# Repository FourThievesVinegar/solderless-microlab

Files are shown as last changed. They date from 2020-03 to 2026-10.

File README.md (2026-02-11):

# MicroLab

The MicroLab is an open-source, DIY, automated controlled lab reactor (CLR) that people can assemble with parts available online. We hope this will do for chemistry what the 3D printer did for manufacturing: provide a DIY, hackable, low-cost method to design and produce certain needful things that otherwise would be out of reach.

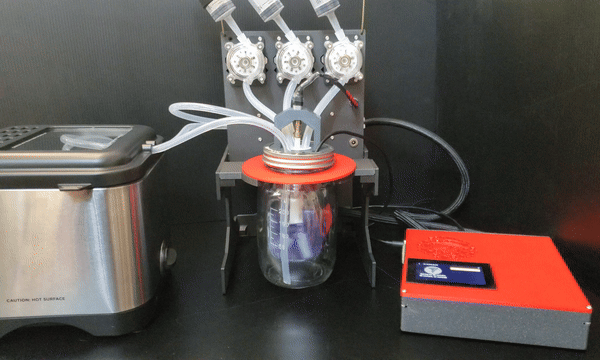
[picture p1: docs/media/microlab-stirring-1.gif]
MicroLab fully assembled with all units


## The MicroLab Suite

For the MicroLab to be accessible to the most people, it was developed as part of a hardware/software stack called the MicroLab Suite. The different software programs help take the information about a compound you want to make and translate it into a recipe (code) that the MicroLab runs to create the compound.

On the [About the MicroLab and MicroLab Suite](docs/motivation.md) page, you can find an introduction to the project with answers to common questions like:
- What the heck is a CLR?
- What's in the MicroLab Suite? 
- And...
- Why we are doing this at all?

MicroLab roadmap of major features for the next 2 versions. V 1.1: “Hello World” recipes complete, Open source reagent pumps, International BOMs, Printable / DIY alternatives for all scarce parts, Atmosphere control. v1.2: Raspberry Pi optional, Recipe repo launched, Auxiliary software suite comple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

In this repo:
```
solderless-microlab
├─ backend/ - Python files for the services that control the state and hardware
├─ design/  - Desktop wallpaper and other design files
├─ docker/  - Docker files 
├─ docs/    - Documentation for the project including build instructions, background, parts list, and troubleshooting
├─ gui/     - React app that runs the GUI 
├─ parts/   - 3d-printable part files for the 1.0+ version
├─ scripts/ - Scripts that start / stop services and flash the Arduino
│  ├─ disk-image - Scripts that build a MicroLab disk image
│  ├─ grbl       - Custom grbl code that allows the Arduino to control the hardware
```

## Architecture

### The Microlab stack

The Microlab is essentially a full-stack web application whose backend has access to control a set of hardware.

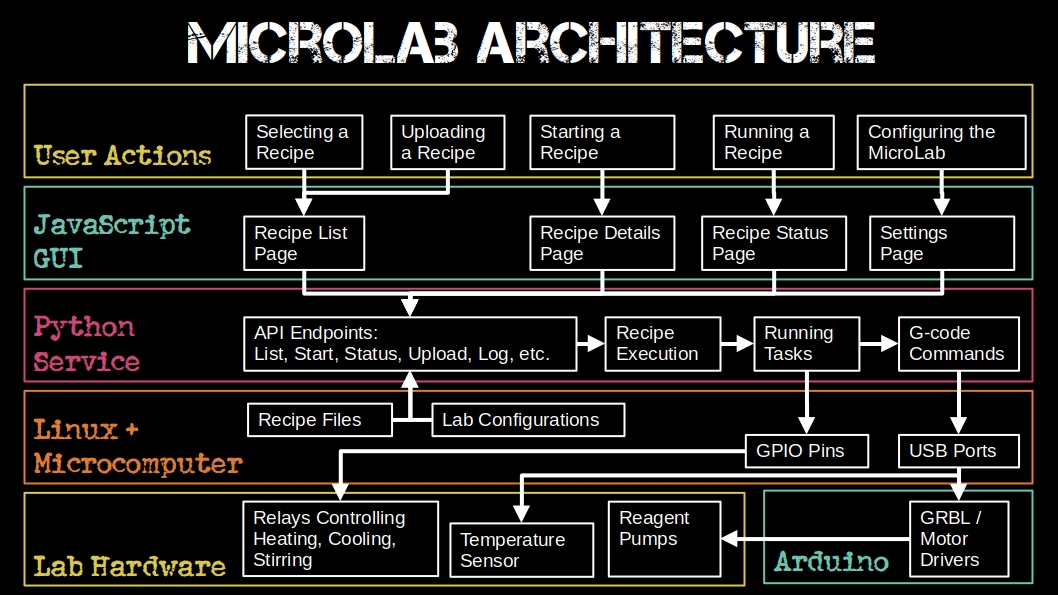
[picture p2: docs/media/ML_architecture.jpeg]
MicroLab architecture diagram. It shows how the user actions, javascript gui, python API, Linux OS, Raepberry Pi micro-computer, and Arduino microcontroller relate to one another.


### Running a Recipe

Running a recipe involves taking user input in the form of a recipe file and tapping on the touchscreen to perform a series of automated and manual tasks to execute a chemical reaction.

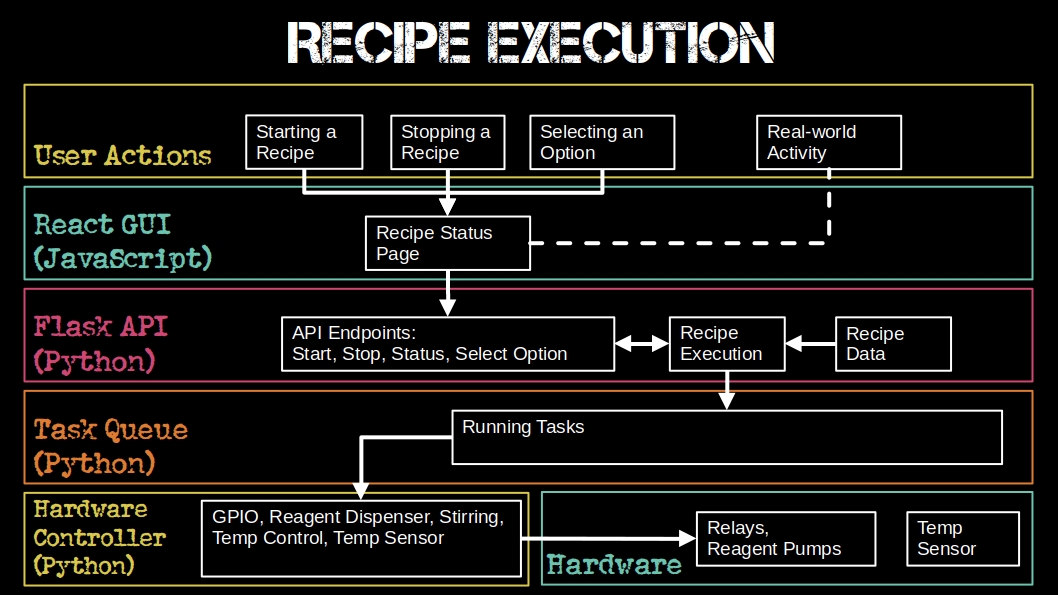
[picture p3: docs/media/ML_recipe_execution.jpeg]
MicroLab recipe flow diagram. It shows how the user actions, javascript gui, python API, python task queue, python hardware controller, and physical hardware relate to one another.


## Getting Started Making Your MicroLab

This section is for you if you want to build a MicroLab and start using it. We tried to make building the MicroLab friendly for folks newer to electronics, but you will need some knowledge and skills with electronics (or the patience to learn a few things).

- Learn [About the MicroLab and MicroLab Suite](docs/motivation.md) so you have an understanding of what you are building.
- **Start here for [How to build & use the MicroLab and MicroLab Suite](docs/index.md)**

## Getting Started Developing the MicroLab

This section is for you if you want to help develop the MicroLab and will need to tinker with the code base. If you're thinking about doing this, be sure to check out the [development wiki](https://github.com/FourThievesVinegar/solderless-microlab/wiki) and the [current issues](https://github.com/FourThievesVinegar/solderless-microlab/issues) planned for development.

You will need to get a copy of the MicroLab software, set up your development environment either with a Docker container, on a Pi, or locally on your computer.

### Installing the MicroLab software locally

Use the instructions below for a fresh install of the MicroLab software on your machine.

If you intend to construct a full MicroLab, [we recommend using our build scripts to make a disk image](https://github.com/FourThievesVinegar/microlab-image). You can also find the latest release of the disk image scripts in this repo in the `/scripts/disk-image` directory. We do not recommend running these scripts directly on the Raspberry Pi. See below if you want to run a development environment on another computer.

## Dev Environment Option 1: Docker Development

For ease of setup/experimentation we added docker containers for both the GUI and the API.
If you don't have docker-compose installed on your system you can install docker desktop following [these docs](https://docs.docker.com/compose/install/)

```bash
git clone https://github.com/FourThievesVinegar/solderless-microlab.git
cd solderless-microlab

## To run API & GUI
docker-compose up --build gui

## Alternatively
## To run just the API
docker-compose up --build api
```

If you're running docker with a hardware setup you'll need to edit docker-compose.yml and uncomment the lines specified in the file.

Docker-compose mounts `docker/microlab-docker.ini` local file as `/etc/microlab/microlab.ini` in the container. To modify microlab config
just edit `docker/microlab-docker.ini` file and restart the container in docker-compose.

For making local development simpler - `backend/` directory is also mounted as container's `/app` directory. Any local file change is automatically reflected in the container but in most cases you would also need to restart container anyway so the python processes load from updated files.

## Dev Environment Option 2: Laptop Setup

Clone the repo:

```bash
git clone https://github.com/FourThievesVinegar/solderless-microlab.git
cd solderless-microlab
```

### API Server

#### Install dependencies:

##### Python

(for Debian / Ubuntu)

```bash
sudo apt update
sudo apt install python3 python3-pip python-virtualenv python3-virtualenv
```

The backend is tested against CPython 3.9 to 3.13.

Note: some versions of Linux have dropped support for Python2 and `python-virtualenv`.

(for macOS)

```bash
brew update
brew install python3
pip3 install virtualenv
```

Set up a Python virtual environment:
virtualenv -p python3 --system-site-packages .venv

```bash
cd backend
virtualenv -p python3 --system-site-packages .venv
source .venv/bin/activate
(env) $ pip install -r requirements.txt
```

##### Install needed packages

(on the Pi)

```bash
sudo apt -y install screen git python3-flask python3-pip python3-serial

```

#### Start the server

```bash
(env) $ python main.py
```

### Web GUI

#### Install dependencies

(for Debian / Ubuntu)

Follow a guide to install yarn for Debian:

https://classic.yarnpkg.com/en/docs/install/#debian-stable

In summary:

```bash
curl -sS https://dl.yarnpkg.com/debian/pubkey.gpg | sudo apt-key add -
echo "deb https://dl.yarnpkg.com/debian/ stable main" | sudo tee /etc/apt/sources.list.d/yarn.list
sudo apt update
sudo apt install yarn
```

(for macOS)

```bash
brew update
brew install yarn
```

#### Run the GUI:

```bash
cd gui
yarn install
yarn start
```

The GUI will now be listening on port 3000.

## MicroLab Hardware Options

### Hardware Emulation

To run the software without a functioning hardware environment, go to the settings menu and change the "MicroLab Controller" setting to "simulation-pi" and "Lab Hardware Config" to "ftv_simulation_microlabv0.5.0"

### MicroLab Setup - Enabling SSH

If you have a MicroLab to run the software on, you may want to enable SSH on the Pi. This makes remote development easier. Instructions for doing so can be found here: https://itsfoss.com/ssh-into-raspberry/

## Start Developing

Once your environment is setup, head on over to the [Backend README](/backend)

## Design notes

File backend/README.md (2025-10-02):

# Solderless Microlab Backend

This project is a python service split into two different units. One controls the microlab hardware, and the other provides an API for getting the state of the microlab and for running recipes on it. The Microlab gui is the main consumer of this API.

## Starting up

See README.md in the root directory for instructions on running the service.

## Configuration

Some general configuration for the microlab can be found at `/etc/microlab` after running the backend for the first time.

## Microlab Controller

### Hardware Device Files

To make it simpler to extend support to new devices or alternate lab setups the microlab makes use of yaml files describing the hardware available on the SBC and connected to it. This is split up into two different files, one for the SBC called controller hardware, and the other for lab hardware.

Both of these file types can be selected, downloaded and uploaded from the settings menu of the microlab.

#### Hardware Devices Reference

A reference for the possible hardware devices and the settings used can be seen in the following two files.

[controller_hardware_reference](data/hardware/controller_hardware_reference.yaml)

[lab_hardware_reference](data/hardware/lab_hardware_reference.yaml)

#### Expanding support to other SBCs

If you want to use something other than a pi or the potato, you can do so by creating a custom controller hardware file. [backend/data/controllerhardware/](data/hardware/controllerhardware/) contains the hardware device description for the two currently supported boards which you can reference.

Only a device named `gpio-primary` using some kind of `gpiochip` describing the available gpio ports is needed at the moment.

## Recipes

The microlab by default loads recipes from files located in `/var/lib/microlab/recipes/`. Recipe files can be uploaded to the microlab from the recipes page. See `solderless-microlab/backend/recipes/base.py` for information on the format required for recipe files.

## Hardware Configs

The microlab by default loads configs from files located in `/var/lib/microlab/hardware/`. Config files can be uploaded to the microlab from the settings page. See `solderless-microlab/backend/data/hardware/lab_hardware_reference.yaml` and `backend/data/hardware/controller_hardware_reference.yaml` for information on the format required for lab hardware and controller hardware configs.

## API

The Microlab backend API includes several endpoints described below. This list is incomplete, for more details, see the implementation at
[/backend/api/routes.py](api/routes.py)

### List

`/list` - Returns an array of the currently available recipe names

Example response:

```
["aspirin"]
```

### Get Recipe

`/recipe/<name>` - Returns the full details for a recipe

### Status

`/status` - Returns an object containing the status of the microlab hardware. It provides a human-readable status message, and information on the current recipe's progress.

Example response:

```
{
    "message":"Place 2.0 g salicylic acid in chamber",
    "options":["Done"],
    "recipe":"aspirin",
    "icon":"reaction_chamber",
    "status":"user_input",
    "step":0
}
```

### Start

`/start/<name>` POST - Starts the recipe with corresponding name

Example responses:

```
{"response":"ok"}
```

or, if you try to start a recipe when one is running:

```
{"message":"Recipe aspirin is running. Stop it first.","response":"error"}
```

### Stop

`/stop` POST - Stops the current recipe

### selectOption

`/selectOption` POST - When in a recipe in a user_input step, select an option

### uploadRecipe

`/uploadRecipe` POST - Upload a JSON file to the microlab.

File must be valid JSON.

### controllerHardware

`/controllerHardware` - Gets the currently configured controller hardware name

### controllerHardware/list

`/controllerHardware/list` - Lists possible controller hardware name

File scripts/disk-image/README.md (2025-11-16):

# microlab-image

**microlab-image** provides everything needed to build a Raspberry Pi OS image pre-configured for the solderless-microlab.

## Repository layout

- **.github/workflows** – CI to build & publish nightly Pi images  
- **config/** – bootloader and kernel-args overrides  
- **overlays/** – rootfs overlay (scripts, notebooks, configs)  
- **scripts/** – image assembly and provisioning scripts  

## Prerequisites

- *nix 
- Docker (Rancher Desktop, Docker Desktop, etc)

## Quick start

```bash
# 1. Clone
git clone https://github.com/FourThievesVinegar/microlab-image.git
cd microlab-image

# 2. Build
#  Follow `BUILD.md`

# 3. Flash
#    resulting image lives in build/raspios-microlab.img
```

## Raspberry Pi default credentials

* User: thief
* Password: vinegard

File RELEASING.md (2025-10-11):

# Performing a Release of the MicroLab

The MicroLab is an open source hardware/software project with many moving parts. This document is a concise guide for how to go about creating a releasing a stable version.

## Preparing for Release

- Build the latest disk image using [the scripts here](https://github.com/FourThievesVinegar/microlab-image/blob/main/BUILD.md).
- Perform end-to-end testing on a completed unit. Typically this will mean running a test recipe such as Caffeine Extraction on an assembled unit. A mock unit can also be used (for example, one that switches LED's instead of running pumps and motors) but nothing brings out the bugs like a real-life test that does some sort of actual chemistry.
- Make sure that documentation is up to date, including the main README.md, CHANGELOG.md, and any instructions in the docs folder.

### Removing extraneous data

If you are shipping or imaging a device you have logged into and messed with, you may want to remove your development bash history. You can do so with the following command:

```bash
history -c && history -w
```

You may want to remove wifi networks you have logged into. Check `/etc/wpa_supplicant/wpa_supplicant.conf` for saved networks and delete any that you don't want people to know about.

## Doing the Release

- Make a stable branch off of `main`, cherry-pick to it if you make last-minute changes. Use a name like v0.6.0 or v1.0.0 - Use semantic versioning.
- Update version numbers in files as appropriate and update the CHANGELOG document as well.
- Make a release tag for your branch on GitHub.

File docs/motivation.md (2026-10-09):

# About the MicroLab and the MicroLab Suite

## Motivation

Our goal is to build an open-source DIY controlled lab reactor that people can assemble with parts available online. We hope this will do for chemistry what the 3D printer did for manufacturing: provide a DIY, hackable, low-cost method to design and produce certain needful things that otherwise would be out of reach.

Eventually, we hope this will allow people to make certain medicines at home. We also hope it will empower them to believe more deeply in their own bodily autonomy. This is in line with our mission to deliver a de facto "Right to Repair for the human body" as a way of enabling *harm reduction for the living*.

## What is a Controlled Lab Reactor?

Lab reactors provide a controlled environment for conducting chemical reactions, mixing, dispersing, and homogenizing processes. Lab reactors come in various designs, when they are automated they are called Controlled Lab Reactors (CLR).

A commercial CLR looks like this:

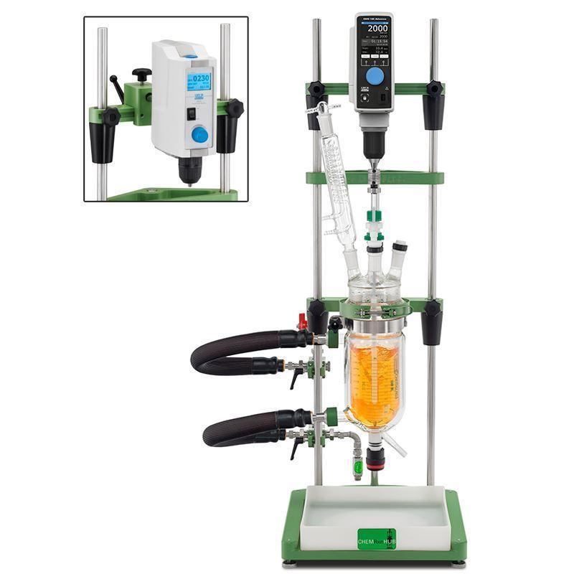
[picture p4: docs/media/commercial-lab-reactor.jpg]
commercial lab reactor


But it costs thousands of dollars and is only available to labs for purchase.

Its reaction vessel looks like this:

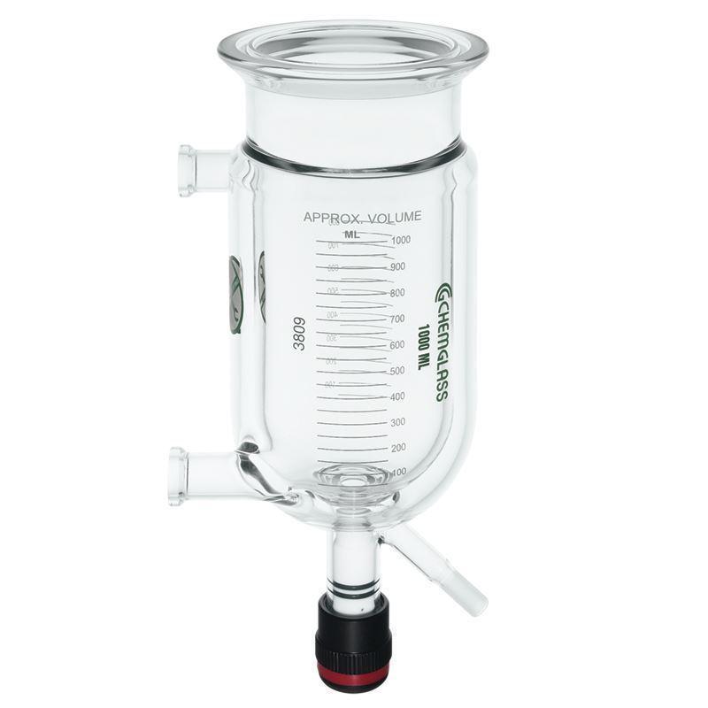
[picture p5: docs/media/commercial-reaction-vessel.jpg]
commercial reaction vessel


The reaction vessel has 2 chambers nested together, a bit like stacked bowls. The reactions happen in the inner chamber. The outer chamber (sometimes called the jacket) has hot or cold liquid pumped in to it to control the temperature. To reaction vessel is covered and reagents are dispensed through ports in the lid. There is a stirring rod in the center.

## Why Use a CLR?

You don’t need a CLR to make chemical reactions happen, but it makes the process of synthesizing compounds from precursors much easier and more reliable.

A CLR is to organic chemistry what an espresso machine is to coffee. It is possible to make coffee over an open fire with nothing more than beans, water, and a tin can. But you will get a better, more consistent cup of coffee from an automatic machine that dispenses the right amount of water at the right temperature in such a way that ensures the water is in contact with the grounds for the right amount of time.

## Commercial CLR vs. MicroLab

Commercial CLRs are the equivalent of high end, fully automatic espresso machines. As long as the appropriate reservoirs are filled with beans, water, milk, and flavoring, anyone can consistently craft a quality cappuccino at the touch of a button.

The MicroLab is more like a home espresso machine that will let you reliably make a good cappuccino but won’t do every single step for you. For both the espresso machine and the CLR you need to understand basic procedures, measurement techniques, and safety.

The MicroLab loads a recipe for a chemical reaction, automatically controls the temperature, adds reagents, and stirs when needed. It is designed for small-molecule organic chemistry to make certain medicinal compounds in your own home or workshop.

## How the MicroLab Works

The MicroLab's Reactor Core has a design similar to a commericial CLR. A 250ml glass bottle is attached to the custom lid for a 32 oz Mason jar. When screwed together the bottle jar is suspended in the 32 oz jar. The lid has ports for reagents, a temperature probe, a stirring rod, and ports for the hot or cold water to be added to the outer vessel.

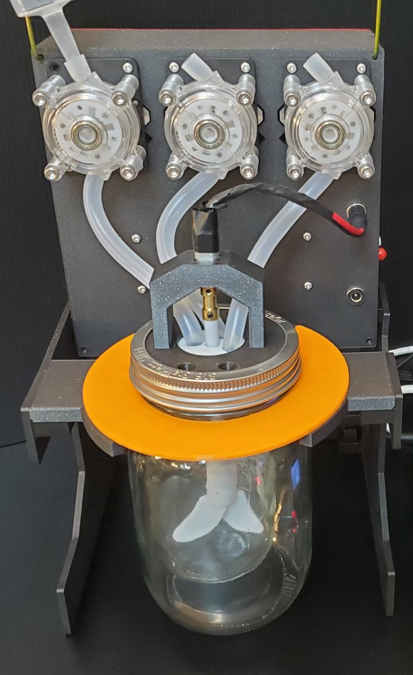
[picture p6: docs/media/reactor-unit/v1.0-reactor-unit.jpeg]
Reactor unit fully assembled


The reagents are held in syringes or other vessels and loaded into pumps powered by stepper motors.
The thermal regulator fluid is delivered by pumps controlled by relays. We heat with a hot plate or deep fryer. We cool with an ice bath or a freezer.

The hardware is driven by a Raspberry Pi, which controls relays and stepper motors used to activate the MicroLab's various features. The parts can be assembled without soldering.

The user selects "recipes" - reactions to run - from an integrated touch screen menu. The recipe guides them, step-by-step, through the reaction, controls the temperature, and automatically dispenses the correct amount of reagents at the right times.

MicroLab fully assembled with all units

## Meet the MicroLab Suite

The microlab suite is a hardware/software stack that enables the full drug development lifecycle from the chemistry itself back through reaction planning.
|||
|-----|-----|
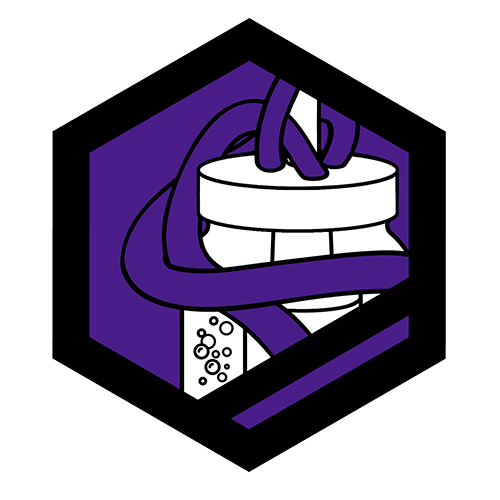
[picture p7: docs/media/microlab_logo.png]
MicroLab
||**The MicroLab** - A DIY automated lab that you download, 3D print, and assemble with commonly available hardware. The MicroLab works together with a suite of apps to guide and automate a variety of lifesaving drugs from your home.|
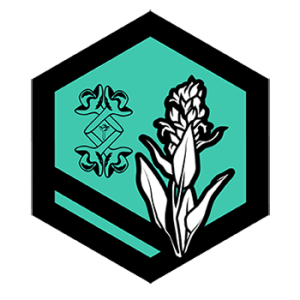
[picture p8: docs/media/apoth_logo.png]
Recipe Press
|  | **Recipe Press** - A simple web app to create "recipes" - sets of instructions the MicroLab uses to run chemical reactions. Best accessed through Vinni (see below). |
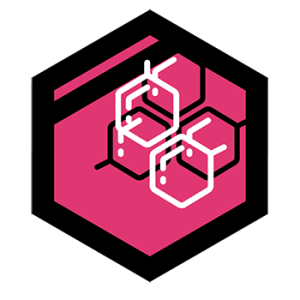
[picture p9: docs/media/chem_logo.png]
Chemhacktica
|  | **[Chemhacktica](https://synth.fourthievesvinegar.org/)** - A tool that uses machine learning to automagically discover reaction pathways to target compounds. Please use the link gently, it's our development server. |
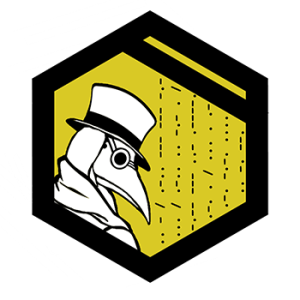
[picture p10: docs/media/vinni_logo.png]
Vinni
|  | **[Vinni](https://vinni.fourthievesvinegar.org/)** - Your guide to your new medical laboratory. Vinni keeps track of your projects including "recipes" from the Recipe Press and compounds of interest from Chemhacktica. (Please note that as of Oct 2026 this is and may ever remain an early alpha) |
|||

## Being the change we want to see in the Cyberpunk Dystopia

In our current situation, closed-source, opaque, unaccountable systems govern us from afar. We live our lives at the mercy of the state, the dollar, and the algorithm. These forces smile benevolently on some while they ignore or discipline others. With this project, we hope to nudge the world toward a future where each of us can help and heal one another and ourselves directly, without the need to grovel before modern day gods and masters.

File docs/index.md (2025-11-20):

# Welcome to The MicroLab

The MicroLab assembled

The MicroLab is part of the MicroLab Suite. Learn more about the hardware/software stack [here](/docs/motivation.md#Meet-the-MicroLab-Suite)

The MicroLab is made up of:

- **Control Unit** - Runs the software and controls the hardware
- **Heating Unit** - Heats the liquid that circulates in the Reactor Core to warm it
- **Cooling Unit** - Cools the liquid that circulates in the Reactor Core to cool it
- **Reactor Unit** - Reactor Core, Pumps Box, and Reactor Stand assembled together
  - Reactor Core - made up of the inner chamber (small glass bottle) where compounds are made, outer chamber (large glass jar) where liquid circulates to warm or cool the inner chamber, thermistor to take temperature in the inner chamber, stir rod to mix things in the inner chamber, and the parts to mount and hold all the pieces together
  - Pumps Box - houses the circulating pumps, peristaltic pumps and two ports, one for the stir rod and one as an additional accessory port

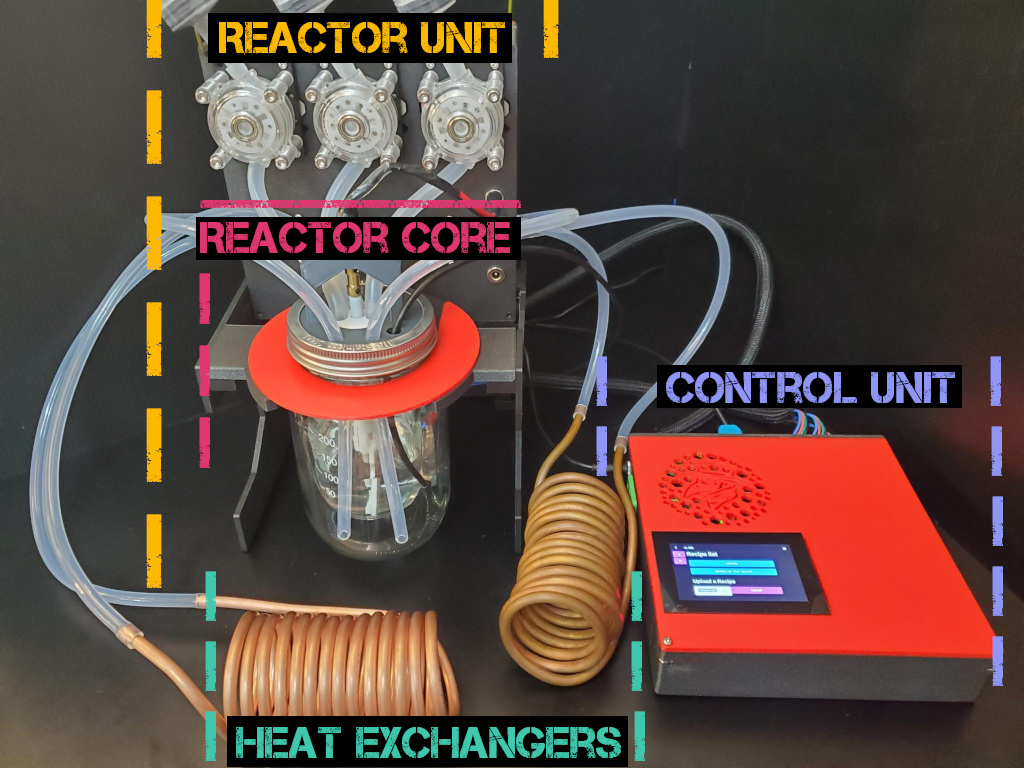
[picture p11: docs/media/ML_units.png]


If you are having trouble with your MicroLab, check out our [troubleshooting guide](https://github.com/FourThievesVinegar/solderless-microlab/blob/main/docs/troubleshooting.md).

## Index

- [About the MicroLab and MicroLab Suite](/docs/motivation.md)
- [Welcome to the MicroLab](/docs/index.md) <-- You are Here
  - [Purchased Parts](#purchased_parts)
  - [Printed Parts](#3d)
  - [Building the MicroLab](#build)
  - [Using the MicroLab](#use)
  - [Resources](#resources)

## Parts

### Purchased Parts

We created a parts list with all the purchased and printed parts that you will need to build a MicroLab.

For the purchased items, we have links to one or more sources. We used the links more as reference so you can see the item and specifications. We did not optimize for price or local availablity. We encourage everyone to look for the best price and supplier for themselves.

Get the file here: [The MicroLab's Parts List](https://github.com/FourThievesVinegar/solderless-microlab/blob/main/docs/parts-list.md)

### Printed Parts

The MicroLab uses several custom parts, which are listed on the [parts list](https://github.com/FourThievesVinegar/solderless-microlab/blob/main/docs/parts-list.md). The raw and printable files for these parts can be found on the [MicroLab Parts Github repo](https://github.com/FourThievesVinegar/microlab-parts/tree/master/v7).

Below are quick links to the repo for the printable parts. These files have the extension .stl at the end. The STL file format is what slicer software uses to make the instructions for the 3D printer.

No 3D printer? If you do not have a 3D printer, there are a few options including:

- Have a friend with a 3D printer print the parts.
- Check if a local library or makerspace has a 3D printer you can use -- and maybe get help with printing.
- Realistically, you can make most of the printed parts (but probably not the reactor core!) out of a material like wood or corrugated plastic. If you use alternate materials, be sure to double-check that the stand is strong enough and that all of the components will be protected and supported. You can use conventional standoffs to support the electronic components if you can't print the control unit case.
- Use an online 3D printing service. We don't endorse any service but have linked a couple sites below as a starting point. We urge you to look at reviews and get quotes to find the best option for you.
  - https://www.pcbway.com/rapid-prototyping/manufacture/
  - https://www.shapeways.com/

**Printable Files (STLs) for the 3D Parts**

- Control Unit
  - [Case for the Control Unit](https://github.com/FourThievesVinegar/microlab-parts/blob/master/v7/control-box/control-box-v.1.0.stl)
  - [Lid for the Control Unit Case](https://github.com/FourThievesVinegar/microlab-parts/blob/master/v7/control-box/control-box-lid-v.1.1.stl)
  - Internal Subcomponents - [Case for the 4-channel Relay Board and 12v to 5v converter](https://github.com/FourThievesVinegar/microlab-parts/blob/master/v7/control-box/sub-components/relay-board-case-50x73x17mm-no-top.stl)
  - Internal Subcomponents- [Case for the 12V to 5V Converter](https://github.com/FourThievesVinegar/microlab-parts/blob/master/v7/control-box/sub-components/stepdown-case-63x27x14mm.stl)
- Reactor Unit
  - Pumps box
    - [Box for the Pumps](https://github.com/FourThievesVinegar/microlab-parts/blob/master/v7/pumps-box/pumps-box-v.1.1.stl)
    - [Lid for the Pumps Box](https://github.com/FourThievesVinegar/microlab-parts/blob/master/v7/pumps-box/pumps-box-lid-v0.4-no-connectors.stl)
  - Reactor Core
    - GL-45 Version
      - [See STL files and assembly instructions here.](https://github.com/FourThievesVinegar/microlab-parts/tree/master/v7/reactor-manifold-GL45)
  - Reactor stand
    - [Piece 1: H shape](https://github.com/FourThievesVinegar/microlab-parts/blob/master/v7/reactor-stand/reactor-stand-H.v1.0.stl)
    - [Piece 2: A shape](https://github.com/FourThievesVinegar/microlab-parts/blob/master/v7/reactor-stand/reactor-stand-A.v1.0.stl)
    - [Piece 3: ¢ shape](https://github.com/FourThievesVinegar/microlab-parts/blob/master/v7/reactor-stand/reactor-stand-c.v1.0.stl)
    - [Piece 4: K shape](https://github.com/FourThievesVinegar/microlab-parts/blob/master/v7/reactor-stand/reactor-stand-k.v1.0.stl)
    - [Piece 5: Jar flange shape (2)](https://github.com/FourThievesVinegar/microlab-parts/blob/master/v7/reactor-stand/reactor-stand-jar-flange.v0.1.STL)
  - Syringe Pumps (if not using peristaltic pumps)
    - [See STL files and assembly docs here](https://github.com/FourThievesVinegar/microlab-parts/tree/master/syringe-pump)

## Building the MicroLab

Use the following index to build the units and then assemble into the MicroLab

1. [Building the Control Unit](/docs/assembly-control-unit.md)
1. [Building the Heating and Cooling Units](/docs/assembly-temperature-exchangers-unit.md)
1. [Building the Reactor Unit](/docs/assembly-reactor-unit.md)

## Using the MicroLab

- [Setting up and using the MicroLab](/docs/operation.md)

## Resources

[MicroLab Suite - Vinni](https://vinni.fourthievesvinegar.org/projects/NVXg2yPAKaMu)
[MicroLab Suite - Recipe Press](https://recipepress.fourthievesvinegar.org/)

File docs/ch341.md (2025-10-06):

# How to configure connections with Arduinos based on the CH341 chip

1. run:
    ```shell
    sudo tee /etc/udev/rules.d/99-microlab.rules << 'EOF'
    # Give the CH340 clone a non-default priority of 10
    SUBSYSTEM=="tty", ATTRS{idVendor}=="1a86", ATTRS{idProduct}=="7523", SYMLINK+="arduino_usb", OPTIONS+="link_priority=10"
   
    # Give the official Arduino Uno a higher priority so it wins the link
    SUBSYSTEM=="tty", ATTRS{idVendor}=="2341", ATTRS{idProduct}=="0043", SYMLINK+="arduino_usb", OPTIONS+="link_priority=20"
   
    SUBSYSTEM=="tty", ATTRS{idVendor}=="1a86", ATTRS{idProduct}=="5523", SYMLINK+="thermometer_usb"
    EOF

    sudo chown root:root /etc/udev/rules.d/99-microlab.rules
    sudo chmod 644       /etc/udev/rules.d/99-microlab.rules   
    ```

2. Reboot Raspberry Pi

3. Select [ch341-pi.yaml](../backend/data/hardware/controllerhardware/ch341-pi.yaml) as `Lab Hardware Config` file

4. Select [ch341_ftv_microlabv0.5.0.yaml](../backend/data/hardware/labhardware/ch341_ftv_microlabv0.5.0.yaml) as
   `Microlab Controller` file

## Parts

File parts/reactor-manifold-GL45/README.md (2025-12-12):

# GL45 Variant Reactor Core

This design uses a borosilicate media bottle with GL45 threads as the inner vessel and a hand-cut teflon disk as the lid to improve chemical compatibility. Because the sealing surface is the bottom of the teflon disk, not the edges, tight tolerances are not required.

## Parts

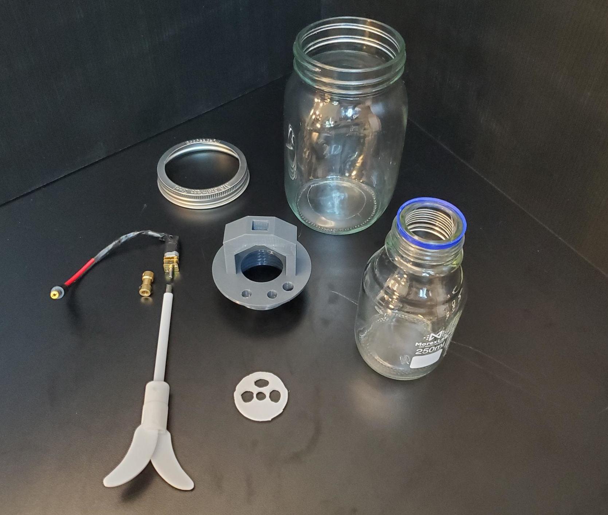
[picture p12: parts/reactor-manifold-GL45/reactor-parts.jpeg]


Reactor Core parts list:

- Outer Jar and lid ring
- Inner 250ml GL45 borosilicate bottle
- Printed Reactor Core
- Carved PTFE Disc
- PTFE stirrer
- Shaft coupler.
- Motor with barrel plug attached

Refer to [the parts list](https://github.com/FourThievesVinegar/solderless-microlab/blob/main/docs/parts-list.md) for exact specifications and notes.

## PTFE Disc

The disc itself is approximately 35mm in diameter. The stirrer in the parts list requires a central hole approximately 8mm in diameter. The reagent pump tubes have an outside diameter of 10mm. While it is possible to drill PTFE, it is much easier to work it with a knife.

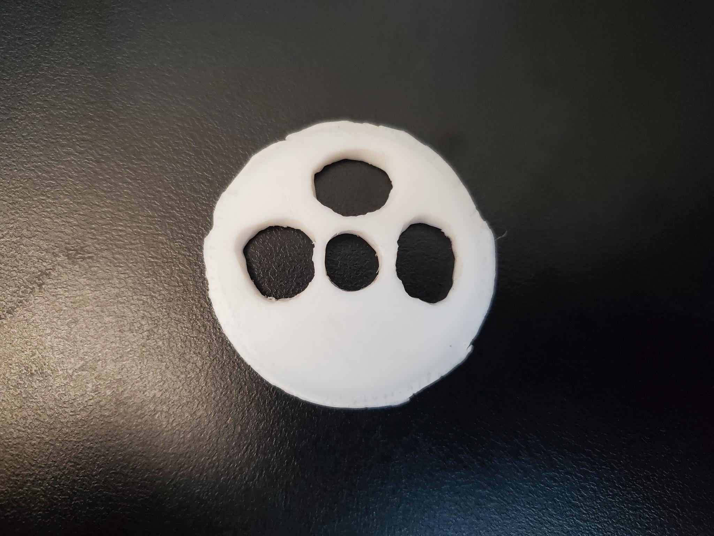
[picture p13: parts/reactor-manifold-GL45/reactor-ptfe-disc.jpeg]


## Assembled

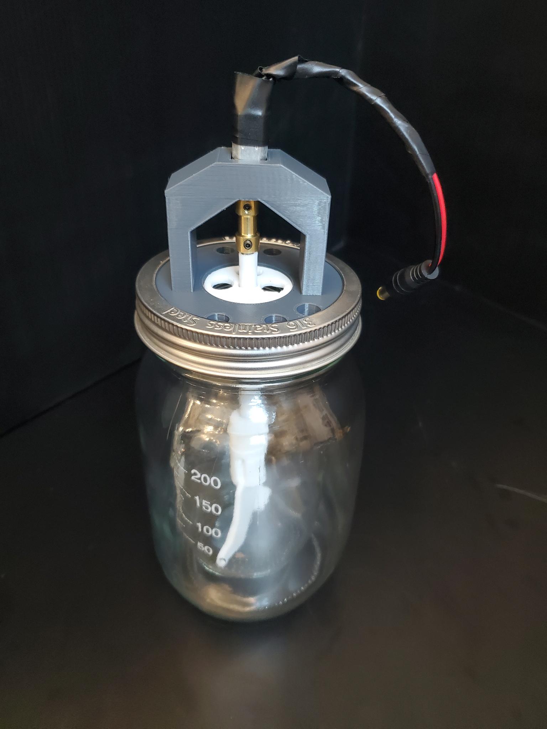
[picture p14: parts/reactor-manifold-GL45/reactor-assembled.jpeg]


## Increasing Temperature Tolerance

The temperature tolerance of the Reactor Core is a major reason for the transition to this new design. In order to increase tolerances further, we have conducted annealing experiments involving heat treating the part. Based on these experiments, we recommend the following:

- Print the part in PETG filament, which has more thermal resistance than PLA. If you have used other materials, and especially if you have conducted temperature tests, please contact us with your findings. 
- Anneal the PETG manifold in an oven for 60 minutes at 185°F / 85°C.
- This will cause the part to shrink in the X/Y dimensions and expand slightly in the Z direction. To account for this deformation, we recommend scaling the model to 103.5% in the X and Y dimensions while scaling it to 97.5% in the Z dimension.

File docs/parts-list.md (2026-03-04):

# MicroLab Parts List

NOTE 1: We link to places that have the parts that we used. They aren't picked for best price or universal availability
NOTE 2: Saving money - check the price of a part in multiples, it may be cheaper than buying just one

## CONTROL UNIT (CU)

|  Part ID	| Count	| Name	        | Primary Link    |	Secondary Link |	Description / Notes |
| --------  | --    | ------------- |  -------------  | -------------- | -------------- |
| CU-RPI	  | 1	    |Raspberry Pi 3 Model B Board |	[Amazon link](https://www.amazon.com/ELEMENT-Element14-Raspberry-Pi-Motherboard/dp/B07BDR5PDW)	| [Amazon Le Potato link 2](https://www.amazon.com/gp/product/B0BQG668P6)|	Primary link is to a Raspberry 3b+'s which is the most extensively tested.   Second link is for devlopers, we have experimental support for Le Potato by Libre Computer (link2). |
| CU-SCR	    | 1	    |Touchscreen for Raspberry Pi	| [Amazon link](https://www.amazon.com/dp/B0DQD3RFCT)|  |		Touchscreen for Raspberry Pi (CU-RPI). 3.5" display with DSI cable compatibility.  Minimum recommended screen resolution is 640 x 480. |
| CU-SD32	| 1	| Micro SD card, 32GB |	[Amazon link](https://www.amazon.com/SanDisk-Extreme-microSDHC-Memory-Adapter/dp/B06XYHN68L/)| |		32GB is the minimum. If you make a new image on a larger card, you can use Pi Shrink to remove empty space from the disk image. If you shrink to the minimum, you may need to re-expand or your partition will run out of space|
| CU-UPC	| 1	 | Micro USB Cable, right angle |	[Amazon Link](https://www.amazon.com/Durable-Braided-Android-Charging-Samsung/dp/B09XK4JDBJ) |	|	Power cable for Raspberry Pi (CU-RPI). The right angle (90 degree) connector will fit better in the Control Unit case. You will need a cable that fits your Pi, we linked to a Micro USB (although newer board usually use USB C). |
| CU-UNO	| 1	| Arduino UNO	| [Amazon link (kit)](https://www.amazon.com/DAOKI-Expansion-Arduino-Heatsink-Engraving/dp/B08KFYKKN4) - be sure to pick option with UNO board	| [Amazon link](https://smile.amazon.com/Arduino-A000066-ARDUINO-UNO-R3/dp/B008GRTSV6/) |	Links to kit will include Uno, CNC shield, motor drivers modules andle USB A/B cable. |
| CU-CNC	| 1 | 	Arduino CNC shield	| Included in kit	| | |	
| CU-SMD |	3	| Stepper Motor Drivers [For CU-CNC]		| Included in kit | | |
| CU-A2B	| 1	| USB A/B cable for Raspberry Pi to Arduino | Included in kit | | |			
| CU-RLY |	1 |	4-Channel Relay Board	 | [Amazon link](https://www.amazon.com/gp/product/B07BDJJTLZ/) | | |		
| CU-WCL	| 1	| Wire Connector (lever), 2-in-6-out	 | [Ali Express link](https://www.aliexpress.us/item/3256805430655743.html) | 	[Amazon link](https://www.amazon.com/gp/product/B08QMLSMC6) - assortment	| Called the 12V Wire Connector. The 2-in-6-out wire connector is used for 12V wiring. The 65-pack in the second link is enough to make multiple MicroLabs, smaller packs are avaiable but will be a higher cost per connector. This part is makes the wiring easier, but it can be replaced by any reliable method of splicing wires. |
| CU-JMP	| 5	| Breadboard Jumper Wires, male-female	| [Amazon link](https://www.amazon.com/Elegoo-EL-CP-004-Multicolored-Breadboard-arduino/dp/B01EV70C78) | |		Small wires to connect the pins on the Pi to other components.  |
| CU-POW	| 1	| Power Supply, 12V 5A	| [Amazon link](https://www.amazon.com/gp/product/B07GFFG1BQ)	| 	| This a 12v 5A power brick. If you’ve got one from an old laptop with a 5.5 x 2.1 mm plug, it may work just fine. Powers the MicroLab. |
| CU-CBC	| 1	| Control Case (Printed)	| Check the `/parts` directory	| [Github Link](https://github.com/FourThievesVinegar/microlab-parts/tree/master/v7/control-box)	| The docs index page goes into more detail about the 3D printed parts. |
| CU-CBL	| 1	| Control Lid (Printed)	| Check the `/parts` directory	| [Github Link](https://github.com/FourThievesVinegar/microlab-parts/tree/master/v7/control-box)	| The docs index page goes into more detail about the 3D printed parts. |
| CU-CCP	| 1	| Converter case (Printed)	| Check the `/parts` directory	| [Github Link](https://github.com/FourThievesVinegar/microlab-parts/tree/master/v7/control-box/sub-components) |	The docs index page goes into more detail about the 3D printed parts. 
| CU-RCP	| 1	| Relay case (Printed)	| Check the `/parts` directory	| [Github Link](https://github.com/FourThievesVinegar/microlab-parts/tree/master/v7/control-box/sub-components) |	The docs index page goes into more detail about the 3D printed parts. 
| CU-PLG  |	3	| Barrel plug connectors, 5.5mm x 2.1mm	| [Amazon link](https://www.amazon.com/gp/product/B08SJM2G52)| |		Connector with wires, 1 female and 1 male. Used for power on the control unit and stirrer / auxiliary port on the pumps box |
| CU-USB	| 2	| Mountable USB cables	| [Ali Express Link](https://www.aliexpress.us/item/2261800163146375.html) |	[Amazon Link](https://www.amazon.com/Extension-Various-Chassis-Cabinets-Extender/dp/B09SQ86ZJM/?th=1)	| Straight connectors will work best, shorter length (25cm) is recommended. |
| CU-SDC	| 1	| 12V to 5V Converter, stepdown |	[Amazon link](https://www.amazon.com/gp/product/B07XXWQ49N) |	[Ali Express Link](https://www.aliexpress.us/item/3256805964676363.html)	|Stepdown converter with barrel connector and USB ports. |
|CU-RAH	| 1	| Right angle header row	| [Amazon link](https://www.amazon.com/Right-Female-Header-2-54mm-Connector/dp/B00R1M3JRQ)	|	
| CU-WCS |	1	| Wire Cutter and Stripper| 	[Amazon link](https://www.amazon.com/WGGE-Professional-crimping-Multi-Tool-Multi-Function/dp/B073YG65N2)	|	
| CU-FCT	| 1	| Flush cutters	| [Amazon link](https://www.amazon.com/Hakko-CHP-170-Micro-Cutter/dp/B00FZPDG1K)		
| CU-NNP	| 1	| Needle-nose pilers	| [Amazon link](https://www.amazon.com/Dykes-Needle-Pliers-Cutter-5-Inch/dp/B0733P4KZ5)	|	

## Shared Parts

|  Part ID	| Count	| Name	        | Primary Link    |	Secondary Link |	Description / Notes |
| --------  | --    | ------------- |  -------------  | -------------- | -------------- |
| SP-CAB	| 15ft roll |	4-wire cable, 18 gauge	| [Amazon link](https://www.amazon.com/gp/product/B07SJGHMX2)	|	| [Control Unit] [Pumps Box] 10 feet will be used to make cables to connect the Control Unit and the Pumps unit. Some of the rest will be used to wire components within the Control Unit. You can also use wires from ethernet cables.
| SP-RBW	| 40ft  roll	| 2-wire cable, red and Black , 18 gauge	| [Amazon link](https://www.amazon.com/TYUMEN-Electrical-Extension-Flexible-Lighting/dp/B01LZRV0HV)	|	| Optional and we won't use all of it, you may want to get a smaller amount if you can find it cheaper. Or just use ethernet cable.
| SP-SWW	| 15ft roll	| Split Wire Wrap, half-inch	| [Amazon link](https://www.amazon.com/AIRIC-10feet-Management-Retardant-Protector/dp/B0BFHT9XG8)		| | [Control Unit] [Pumps Box]
| SP-PC12	| 2	| 12-pin connector, panel-mount screw terminal | 	[Ali Express  link](https://www.aliexpress.us/item/3256805663080411.html)	|	|[Control Unit] [Pumps Box]  connector has three pieces: plug, mount plate and socket
|SP-PC8	| 2	| 8-pin connector, panel-mount screw terminal 	|||		[Control Unit] [Pumps Box] connector has three pieces: plug, mount plate and socket
| SP-PC2	| 1	| 2-pin connector, panel-mount screw terminal |	|	|	[Control Unit] connector has three pieces: plug, mount plate and socket
| SP-M3S-12	| 23	| 12mm M3 screws with nuts (Optional)| 	[Amazon link](https://www.amazon.com/gp/product/B09WMCWPRL/) - assortment	| |	[Reactor Unit] 20 for reactor stand (Optional, for the screw-together version)
| SP-M3S-16	| 28	| 16mm M3 screws with nuts	|||		[Control Unit] [Pumps]  20 for Pumps Box, 8 Control Unit
| SP-M3S-20	| 2	| 20mm M3 screws with nuts	|	|	| [Control Unit] [Reactor]  2 for Control Unit
| SP-M3S-30	| 5	| 30mm | M3 screws with nuts	|	|	Pumps Box 4
| SP-SMC	| 6	| Stepper motor cables	| included w/ peristaltic pumps	|	|The 3 stepper motors come with their own cable, but will need to cut  in half and both ends stripped. The linked ones are ready to use. 
| SP-ETN	| 1 roll	| Electrical tape, narrow	| [Amazon link](https://www.amazon.com/Ancor-Marine-Products-Electrical-Assorted/dp/B01CZ30AY0)	|	| 1" is most common, 1/2" should be narrow enough

## TEMPERATURE CONTROL UNIT

|  Part ID	| Count	| Name	        | Primary Link    |	Secondary Link |	Description / Notes |
| --------  | --    | ------------- |  -------------  | -------------- | -------------- |
| TC-PMP	| 2	| Circulating pump	| [Amazon link](https://www.amazon.com/dp/B09XH1GYYQ)	||	To run both heating and cooling in the same recipe without hardware reconfiguration between recipe steps, 2 pumps are required.  NOTE: Operational limits to pumps in terms of capacity and temperature have not been determined. Larger pumps may be desired for optimal operation, especially at high temperatures. Self-priming pumps are HIGHLY recommended.  NOTE: These will actually be installed in the Pumps Unit.
| TC-CTB	| 2	| Copper tubing 10’ ¼" OD x 3/16" ID	| [Amazon link for raw copper tubing](https://www.amazon.com/dp/B0B6RQ73JQ) |	[Amazon link](https://www.amazon.com/dp/B07FTQJXD7/) for aluminum cooler	| Copper tubing should fit snugly within the silicone tubing. This 10’ length should be enough to make 1 dense or 2 loose heat exchanger coils.   Pre-formed coils used for chilling in beer brewing are more expensive, but easier. These are also typically too large for even wide-mouth mason jars, so another container may be needed. We currently recommend using a countertop deep fryer or robust hot plate for a heat source
| TC-STB	| 1	| Silicone tubing 8mm OD x 5mm ID	| [Amazon link](https://www.amazon.com/dp/B08PTX867M)	|	| Silicone tubing should fit snugly around the copper tubing 
| TC-TAP |	1	| Tape for the insulation|			
| TC-TCT	| 1	| Copper tube cutter tool (optional) |	[Amazon link](https://www.amazon.com/tubing-cutter-brake-line-cutting/dp/B084ZV5BXP)| |	Only required for cutting copper tubing for experimenting with heat exchangers, which is not required.	
| TC-CTJ	| 1	| Copper tube jig	| | | Large dowel or round section of pipe ~5cm dimeter or larger is good       
| TC-LIQ	| 1	 | Liquid, propylene glycol, water, oil, or other	|		| | For temperature exchange with the Reactor Core. We have been using propylene glycol which support temperature ranges as high and as low as the MicroLab supports.

## REACTOR UNIT

|  Part ID	| Count	| Name	        | Primary Link    |	Secondary Link |	Description / Notes |
| --------  | --    | ------------- |  -------------  | -------------- | -------------- |
| RU-SRM	| 1	| Stir rod motor	| [Amazon link](https://www.amazon.com/gp/product/B07FVQ7VPX)	|	[Amazon link](https://www.amazon.com/gp/product/B09XB8TXJC) |  This link is to a 100 RPM 12v motor. You can also buy a faster motor and use a PWM controller to adjust the speed manually.
| RU-STR	| 1	| Stir rod | [Amazon link](https://www.amazon.com/gp/product/B07WRKQY7R)| |		Mixing paddle needs to be coated / PTFE. Stainless steel may react. Paddle should be small enough to fit easily in the 6oz mason jar
| RU-SRC |	1| 	Stir rod coupler | 4mm-to-5mm	| [Amazon link](https://www.amazon.com/dp/B0867R2N1R)		
| RU-PTFE	| 1	| PTFE Sheet	| [Amazon Link](https://www.amazon.com/dp/B094WBY9J6)	|	
| RU-RJF	| 2	| Jar Flanges (Printed)	| Check the `/parts` directory	|	[Github Link](https://github.com/FourThievesVinegar/microlab-parts/blob/master/v7/reactor-stand/reactor-stand-jar-flange.v0.1.STL)	|
| RU-COR	| 1	| 250ml GL45 Borosilicate Glass Bottles	|	[Amazon link](https://www.amazon.com/dp/B09JN683F9) | |	
| RU-OUT	| 1	| 32oz wide mouth mason jar for outer jacket	| [Amazon link](https://smile.amazon.com/Ball-Quart-Silver-Wide-Mouth/dp/B00G9DNO28/)		
| RU-SDH	| 1	| Reactor stand - H  (Printed)	| Check the `/parts` directory	|	Github Link |	H shaped piece for the reactor stand
| RU-SDA	| 1	| Reactor stand - A  (Printed)	| Check the `/parts` directory	|	Github Link	| A shaped piece for the reactor stand
| RU-SDC	| 1	| Reactor stand - ¢  (Printed)	| Check the `/parts` directory	|	Github Link |	¢ shaped piece for the reactor stand
| RU-SDK	| 1	| Reactor stand - K  (Printed)	| Check the `/parts` directory	|	Github Link |	K  shaped piece for the reactor stand
| RU-TMP	| 1	| Thermistor |	[Ali Express link](https://m.aliexpress.com/item/32827261401.html)	| |	Used to monitor the temperature in the reaction chamber. This is a link to a USB DS18B20 
| RU-PPM	| 3	| Peristaltic pumps with stepper motors	| [Amazon link](https://www.amazon.com/gp/product/B082K6CYV1)	| [Alibaba Link](https://www.alibaba.com/product-detail/Peristaltic-Pump-stepper-12V-DC-High_1600102647756.html)	| The 3 stepper motors should come with their own cable, but will need to cut in half and split between the Control Unit and the pumps box.  NOTE: Those links are likely to be sold out. There are other stepper-driven pumps, but they will not interface seamlessly with the printed parts. We’re also looking for DIY/printable designs.
| RU-SYR	| 3	| Syringes	| [Amazon link](https://www.calvetsupply.com/exel-syringe-without-needle-single-syringe-25-cc.html)	||	20 or 30mL are standard sizes. You may want more of these or different sizes.
| RU-PUB	| 1	| Pumps box (Printed)	| Check the `/parts` directory	|	[Github Link](https://github.com/FourThievesVinegar/microlab-parts/tree/master/v7/pumps-box) |	Case to put pumps and motors in 
| RU-PUL	| 1	| Pumps lid (Printed)	| Check the `/parts` directory	|	[Github Link](https://github.com/FourThievesVinegar/microlab-parts/tree/master/v7/pumps-box) |	Lid for pumps case
| RU-SUP	| 1	| Wire coat hanger|||			Used to support the syringes

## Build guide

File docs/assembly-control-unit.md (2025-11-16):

# Control Unit Assembly

We'll start by assembling the brains of the operation, the Control Unit. As the most complex component of the MicroLab, this will take some time and patience.

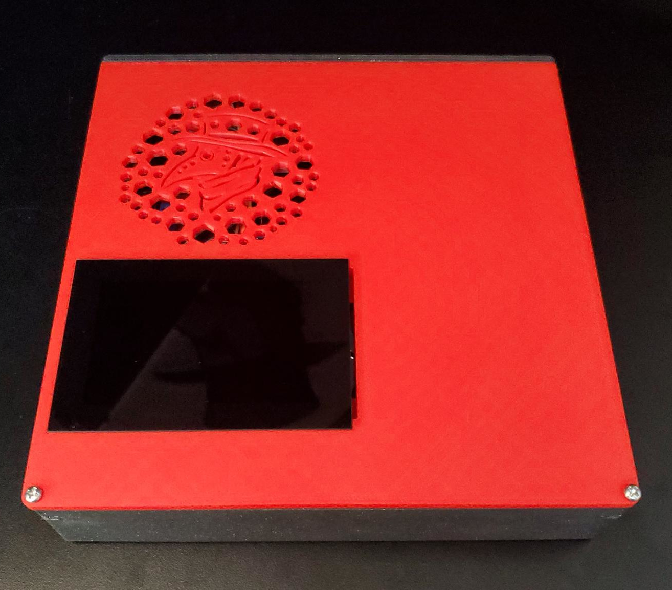
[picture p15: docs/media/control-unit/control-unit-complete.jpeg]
Control Unit
  
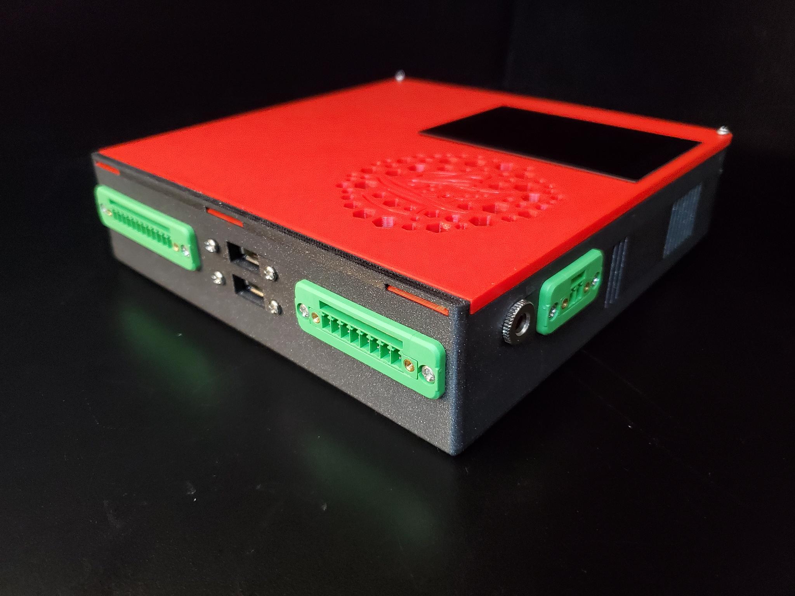
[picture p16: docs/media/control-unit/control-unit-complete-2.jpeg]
Control Unit showing the ports on the back corner
  

To wire things up properly we'll tackle different parts of the Control Unit and then put them all together. We've broken it down by these steps:

* [Setup Control Boards - Raspberry Pi](#raspberry)
* [Setup Control Boards - Arduino](#arduino)
* [Assembling the 12V Circuit](#12V)
   * [Relay Board Wiring](#12vrelay)
   * [Arduino Shield Wiring](#12vshield)
   * [12V to 5V converter Wiring](#12vconvert)
* [Wiring 5V and Signals on the Relay Board](#5vrelay)
* [Mounting Components in the Case](#case)
* [Installing the Components in the Control Unit Case](#installcase)
   * [12V to 5V Converter](#installcon)
   * [Arduino](#installard)
   * [12V Wire Connector](#installwire)
   * [Raspberry Pi](#installpi)
* [Final Assembly](#final)
* [Making MicroLab Cables](#cables)

## Skills Needed

* Wire stripping - one example [video](https://www.youtube.com/watch?v=N__OLJvq2HE)
* Reading pinout diagrams

## Tools Needed

* Wire cutters/stripper (CU-WCS)
* Computer with an SD reader. You may need an SD card to USB converter
* Small phillips head screwdriver for M3 screws, one came in kit on the parts list
* Flush cutters (CU-FCT)
* Needle nose pilers (CU-NNP)

## Parts Needed

**Purchased parts info.** For more information on purchased parts, check the [MicroLab Parts List](microlab-parts-list.xslx).

**Printer parts info.** Parts listed as printed, like "CU-CB Control Case (Printed)", are 3D printed, check the [3D Printed Parts section ](docs/index.md#3d) of the "How to build the MicroLab" page.

| Section | Part ID      | Count      | Part Name | Notes |
|--- | ------------- | ------------- |------| ----|
Control Unit (CU)|	CU-RPI|	1|	Raspberry Pi 3 Model B Board
Control Unit (CU)|	CU-SCR|	1|	Touchscreen for Raspberry Pi
Control Unit (CU)|	CU-SD32|1|	Micro SD card, 32GB
Control Unit (CU)|	CU-UPC|	1|	 Micro USB Cable, right angle
Control Unit (CU)|	CU-UNO|	1|	Arduino UNO
Control Unit (CU)|	CU-CNC|	1|	Arduino CNC shield
Control Unit (CU)|	CU-SMD|	3|	Stepper Motor Drivers [For CU-CNC]
Control Unit (CU)|	CU-A2B|	1|	USB A/B cable for Raspberry Pi to Arduino
Control Unit (CU)|	CU-RLY|	1|	4-Channel Relay Board
Control Unit (CU)|	CU-WCL|	1|	Wire Connector (lever), 2-in-6-out
Control Unit (CU)|	CU-JMP|	5|	Breadboard Jumper Wires, male-female
Control Unit (CU)|	CU-RLY|	1|	4 Channel Relay Board, 5V
Control Unit (CU)|	CU-POW|	1|	Power Supply, 12V 5A
Control Unit (CU)|	CU-CBC|	1|	Control Case (Printed)
Control Unit (CU)|	CU-CBL|	1|	Control Lid (Printed)
Control Unit (CU)|	CU-CCP|	1|	Converter case (Printed)
Control Unit (CU)|	CU-RCP|	1|	Relay case (Printed)
Control Unit (CU)|	CU-PLG|	2|	Barrel plug connectors, 5.5mm x 2.1mm
Control Unit (CU)|	CU-USB|	2|	Mountable USB cables
Control Unit (CU)|	CU-USB|	2|	Mountable USB cables
Control Unit (CU)|	CU-SDC|	1|	12V to 5V Converter, stepdown
Control Unit (CU)|	CU-UTS|	1|	USB to Screw Terminal adapter
Control Unit (CU)|	CU-RAH| 1|	Right angle header row
Control Unit (CU)|	CU-WCS|	1|	Wire Cutter and Stripper
Control Unit (CU)|	CU-FCT|	1|	Flush cutters
Control Unit (CU)|	CU-NNP|	1|	Needle-nose pilers
Shared Parts|	SP-CAB|	15ft roll|	4-wire cable, 18 gauge
Shared Parts|	SP-RBW|	40ft roll|	2-wire cable, red and Black , 18 gauge
Shared Parts|	SP-SWW|	15ft roll|	Split Wire Wrap
Shared Parts|	SP-PC12|	2|	12-pin connector, panel-mount screw terminal
Shared Parts|	SP-PC8|	2|	8-pin connector, panel-mount screw terminal
Shared Parts|	SP-PC2|	1|	2-pin connector, panel-mount screw terminal
Shared Parts|	SP-M3S-12|	23|	12mm M3 screws with nuts
Shared Parts|	SP-M3S-16|	28|	16mm M3 screws with nuts
Shared Parts|	SP-M3S-20|	5	|20mm M3 screws with nuts
Shared Parts|	SP-M3S-30|	5	|30mm M3 screws with nuts
Shared Parts|	SP-SMC|	6|	Stepper motor cables
Shared Parts|	SP-ETN|	1 roll|	Electrical tape, narrow

#### **Prepare Wires**

- The Stepper Motor cables (SP-SMC) should have come with the three peristaltic pumps with stepper motors. Take the 3 cables and cut them in half with the wire cutters.
- Strip both ends on each of the wires (see [Skills Needed](#skills)) for help with stripping wires). Expect to remove 1/4" or more of the insulation. If the lever connector or screw terminal closes on the insulation the electricity won't pass through.
- You should now have 6 cables, three to connect the Arduino to the 12-pin connector in the Control Unit and three to connect the pumps to the 12-pin unit in the Pumps box.

## Control Boards Setup
The Raspberry Pi, a single board computer, and the Arduino, single board microcontroller, are the control boards of the MicroLab.  

The Raspberry Pi runs the show using the MicroLab software and coordinating turning on/off all the different components. The Arduino controls the stepper motors of the peristaltic pumps and gets its instructions from the Raspberry Pi.

### Raspberry Pi Setup

#### Installing the MicroLab software on the Pi
The Raspberry Pi runs its software from the SD card. In this section we will have you install the custom MicroLab disk image which has the Raspberry Pi operating system, the MicroLab software and the touchscreen drivers bundled together.

1. **Install Raspberry Pi Imager.** [Follow the Raspberry Pi website instructions](https://www.raspberrypi.com/documentation/computers/getting-started.html#install-using-imager) to install the Raspberry Pi Imager software onto a computer.
1. **Build the disk image.** Check [this repo](https://github.com/FourThievesVinegar/microlab-image/) for scripts to download and build the MicroLab build image. It can take a few hours to complete, but you will get the latest. There are instructions in the BUILD.md file. You can also find the latest release of the disk image scripts in this repo in the `/scripts/disk-image` directory. We do not recommend running these scripts directly on the Raspberry Pi.
1. **Connect the MicroSD card to your computer.**
1. **Install the MicroLab disk image onto the SD card** [following the Raspberry Pi website instructions](https://www.raspberrypi.com/documentation/computers/getting-started.html#install-using-imager).
   * Be sure to "Use Custom" for the OS and then select the MicroLab disk image.
1. **Verify the disk.** The imager program will run a verification check to make sure the OS was installed correctly. This will take several minutes.
1. **Install the SD card.** Once complete, remove the SD card from your computer, and insert into your Raspberry Pi.
 * **Note:** The SD card extends beyond the edge of the Pi's circuit board.

#### Installing the touchscreen

v1.0 features a new touchscreen. Instead of using the GPIO pins, this one uses the Pi's display port. Instead of attaching to the Pi directly, you will mount the screen to the case lid and connect them using a ribbon cable.

### Arduino Setup

In this section to set up the Arduino board we will:
* Install software that controls the CNC shield
* Attach the CNC shield
* Install the stepper motor driver modules on the shield

Detailed pin diagram here [https://blog.protoneer.co.nz/arduino-cnc-shield-v3-00-assembly-guide/](https://blog.protoneer.co.nz/arduino-cnc-shield-v3-00-assembly-guide/)

**Critical Safety Note:** ALWAYS disconnect the power before connecting or disconnecting the stepper motors from the CNC shield. Failure to do so can hurt both you and the component.

#### Installing the CNC shield controller software

The Arduino Uno board requires the [GRBL](https://github.com/gnea/grbl/) software to control the CNC shield.

We have [a custom version of GRBL](https://github.com/FourThievesVinegar/grbl). The latest release is located in this repository: `/scripts/grbl/` - you can use the instructions there to flash the Arduino with the GRBL firmware.

If you are on the MicroLab and have internet access, you can execute the following script with root permissions from the Raspberry Pi to download and flash the GRBL:

    ```shell
    sudo /opt/solderless-microlab/scripts/flash-grbl-arduino.sh
    ``` 
    NOTE: you can access detailed how-to instructions [here](https://github.com/gnea/grbl/wiki/Compiling-Grbl) to compile and flash ```grbl``` to the arduino manually.

#### Installing the CNC shield controller hardware

 This external video shows the assembly of the CNC shield and stepper motor driver boards. [YouTube Video link](https://youtu.be/zUb8tiFCwmk?t=37)  
    NOTE: We use 3 motor driver modules (the X, Y and Z) while the video shows 4 being installed.

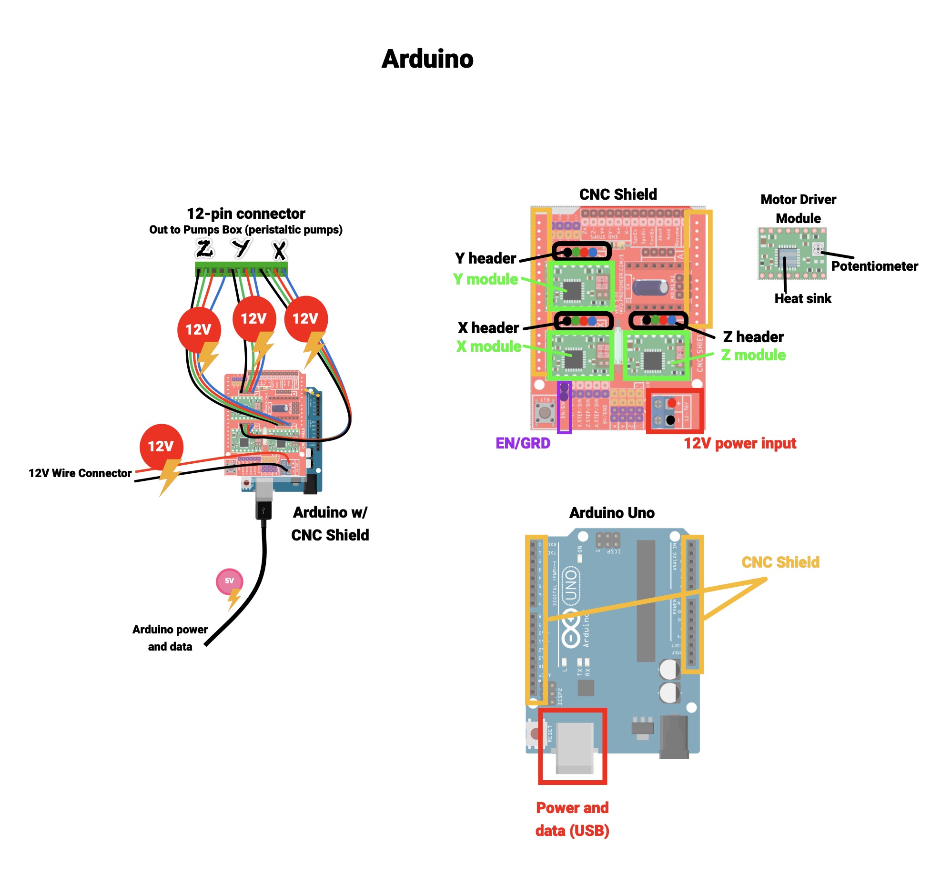
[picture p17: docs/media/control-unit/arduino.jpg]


##### Put the thing on the thing

Place CNC shield on the Arduino, push the CNC pins into the header sockets on the Arduino until it is fully connected. Make sure the shield is oriented such that it lines up with the Arduino and its pins.

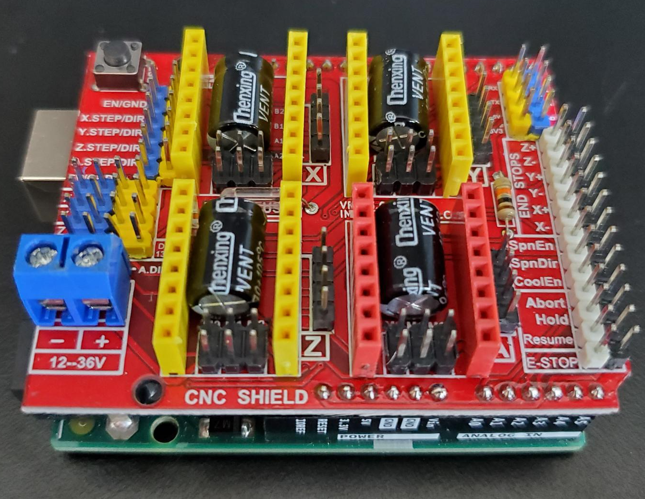
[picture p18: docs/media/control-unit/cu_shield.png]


##### Add Heatsinks to Stepper Motor Driver Modules

Each Stepper Motor Driver module comes with a small heatsink. Peel the adhesive and attach a heatsink to the square black chip on the top of each Stepper Motor Driver module.

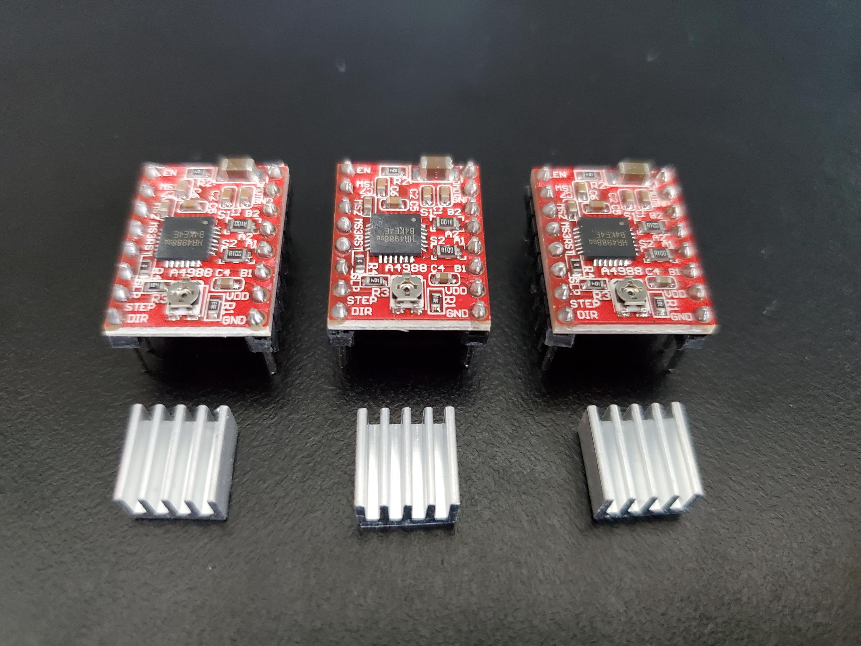
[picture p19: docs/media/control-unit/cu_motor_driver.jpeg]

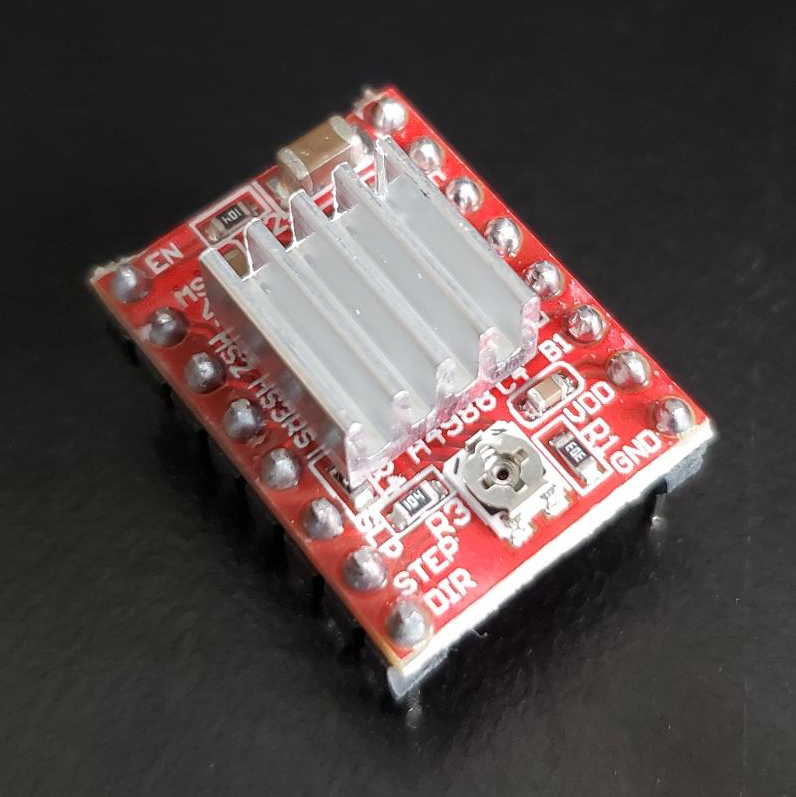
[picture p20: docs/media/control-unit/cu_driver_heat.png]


##### Add the Stepper Motor Driver Modules 

Orient and insert the stepper motors driver boards into the X, Y, and Z slots on the shield.

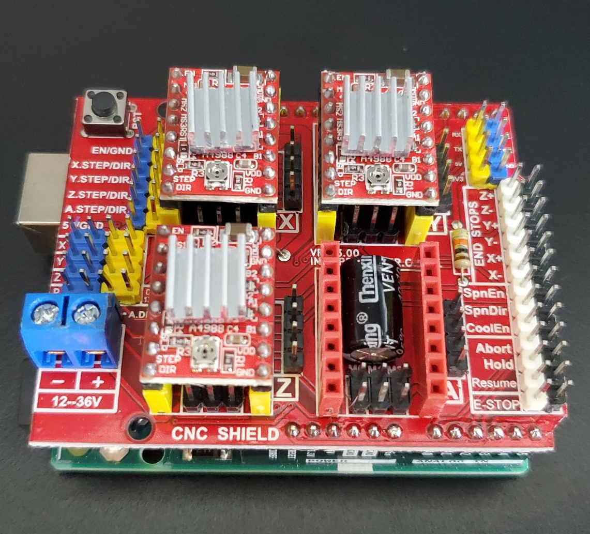
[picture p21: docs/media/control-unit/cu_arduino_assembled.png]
Adding Stepper Motor Driver Boards


OPTIONAL: **Set Enable Pin to Ground.** Place a female-female jumper on the Enable and Ground pins to enable the board.

##### Add Stepper Motor Cables 

The stepper motors cables have a female connector on one end and bare wire on the other. Connect a female connector to the X header, Y header, and Z header on the CNC shield.

## Assembling the 12V Circuit

Time for wiring! This step is where the bulk of the assembling happens for the Control Unit.

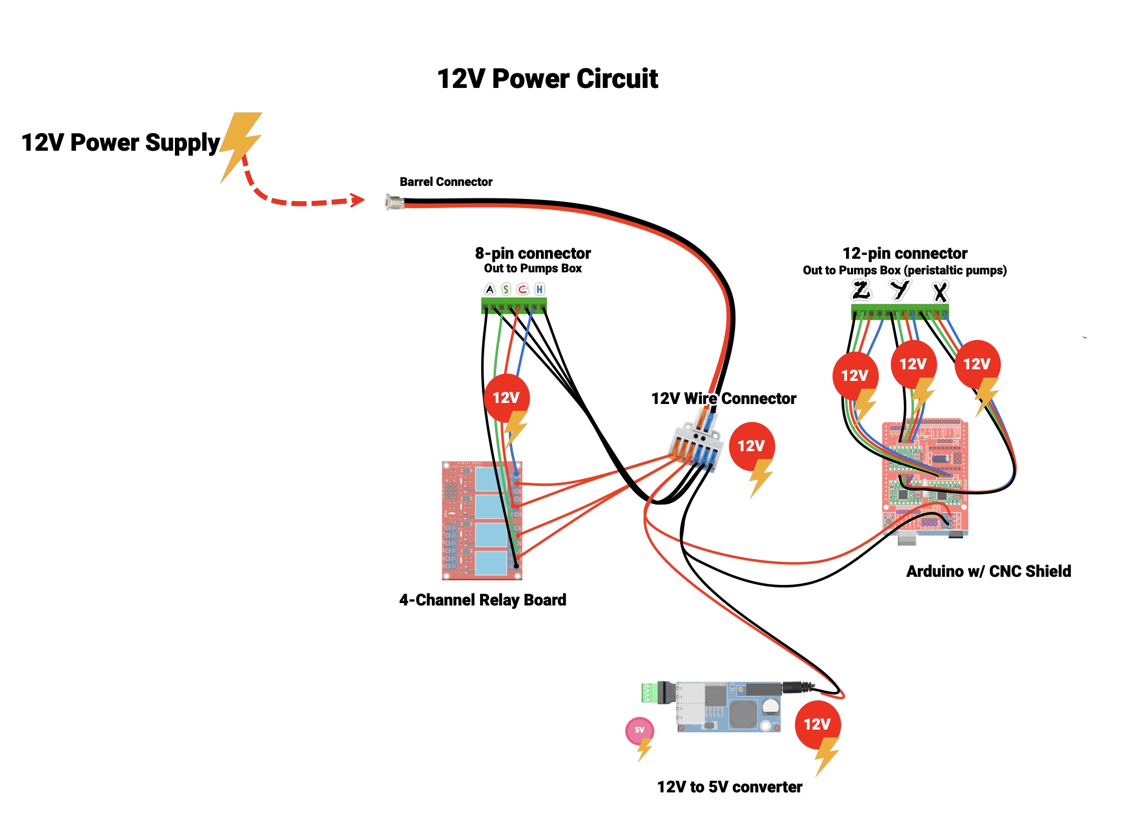
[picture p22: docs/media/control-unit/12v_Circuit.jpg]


The majority of the wires in the Control Unit can be grouped as:
* 12V Power
* 5V Power
* Signals

The 12V circuit is where all the necessary wires are connected so electricity can get from the 12V power supply into the Control Unit and then be sent out at the right time to the 12V components in the MicroLab, specifically:
 * Through the 4-channel relay board to the
    * Heating pump (circulating pump)
    * Cooling pump (circulating pump)
    * Stir rod
    * Accessory port
 * Through the Ardunio shield to the peristaltic pumps
 * To the 12V to 5V converter to provide 5V power

### Relay Board Wiring

In order to send 12V out to components: the 4-channel relay board, the 8-pin connector and the 12V wire connector all connect to each other.

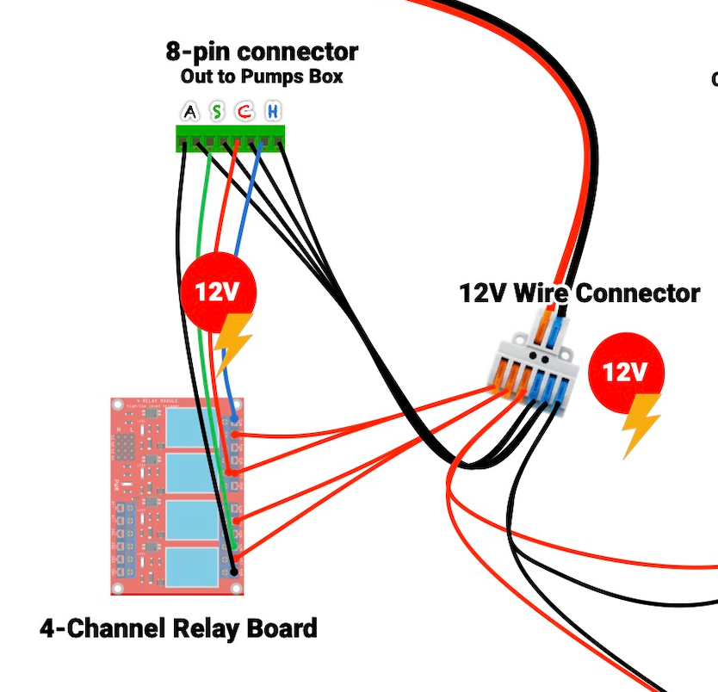
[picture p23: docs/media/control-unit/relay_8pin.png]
8-pin relay sub-assembly parts


#### **Wire Order**

Please read and get comfortable with the wiring order explained on the [MicroLab Wiring](/docs/wiring.md) page. It's important to maintain the same wiring order throughout the project.

**8-pin connector - internal**
The 8-pin connector passes 12V along to the Accessory port (Acc), Stir rod (Stir), Cooling pump (Cool), and Heating pump (Heat) wires.

From inside the case the 8pin connector wiring order will look like this:

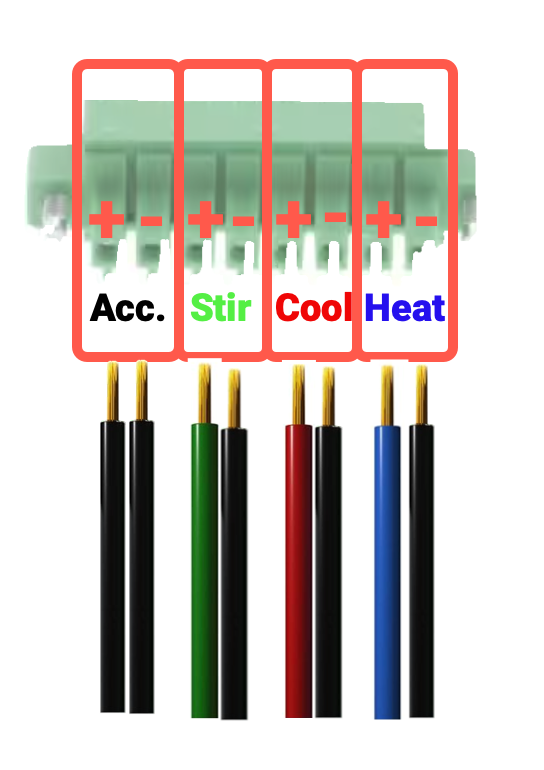
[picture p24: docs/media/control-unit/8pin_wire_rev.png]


#### **Parts**

| Part ID | Part Name  | Count | Notes |
|--- | ------------- | ------------- |------|
|||
SP-PC8|8-pin connector |2
CU-RLY|4 Channel Relay Board|1
CU-WCL|Wire Connector  | 1| Called 12V Wire Connector
CU-JMP|Breadboard Jumper Wires - male-female|5
SP-CAB|4-wire cable |15ft roll| Used to make short wires
SP-RBW|2-wire cable, red and black, 18 gauge |40ft roll| Used to make short wires

#### **Prepare Wires**

- Take the 4-wire cable (SP-CAB) and cut one 4" section and one 6" section.
   - Take the 4" section and separate all four colors (red, blue, green, black)
- Take the 2-wire cable (SP-RBW) and cut one 4" section and four 6" sections
   - Take the 6" sections and separate the red and black wires
- Strip both ends on each of the wires (see [Skills Needed](#raspberry) for help with stripping wires). Expect to remove 1/4" or more of the insulation. If the lever connector or screw terminal closes on the insulation the electricity won't pass through.

You should now have:
- 4" Wires
    - 1 green wire (for 8-pin)
    - 1 blue wire (for 8-pin)
    - 4 black wires (for 8-pin)
    - 4 red wires (for 8-pin)
- 6" wires
    - 4 red wires (for Relay board to the 12V wire connector)
    - 4 black wires (for 8-pin connector to the 12V wire connector)

#### **Wiring the 8-pin connector**
We will attach the positive wires (color coded) and negative wires to the 8-pin connector socket (SP-PC8) first.
* The connectors have 3 pieces: socket, mount plate and plug.

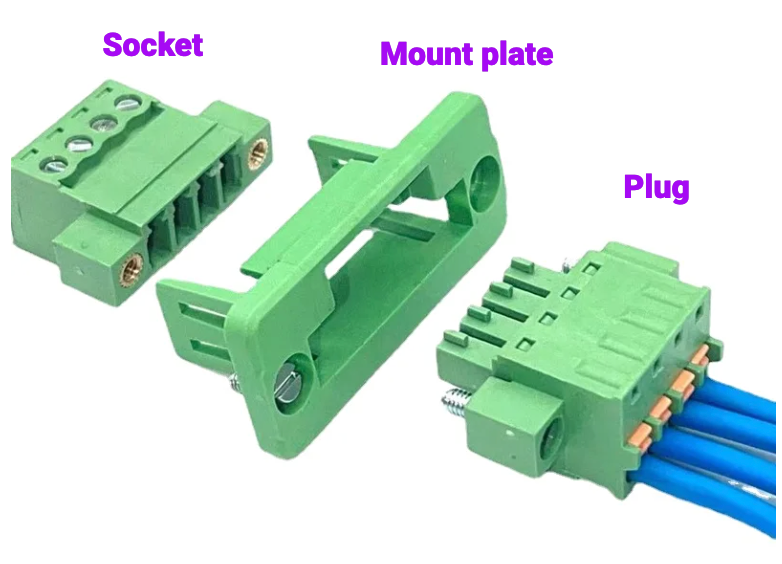
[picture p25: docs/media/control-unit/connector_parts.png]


  - **Wiring the Positives.** Take one of the 8-pin connector sockets and from the back use a small screwdriver to loosen the 8 screw terminals. Working left to right, insert the 4" black, green, red, blue wires into the correct positive (+) terminals and tighten the terminals. Use the photo below or the [wiring order](/docs/wiring.md) page to confirm placement.
    - Don't overtighten the screw terminal. Once done you should be able to lightly tug on the wires without them moving.  

- **Wiring the Negatives.** Next on the 8-pin socket, insert the 6" black cables into the negative (+) terminals and tighten the terminals.
  Cable order
- **Connecting the negative wires.** Take the 12V Wire Connector, open the first two lever slots on the negative side of the connector (shown as the right side with blue levers in our picture). Take the 8-pin negative wires, put two wires in each slot and close the slots.

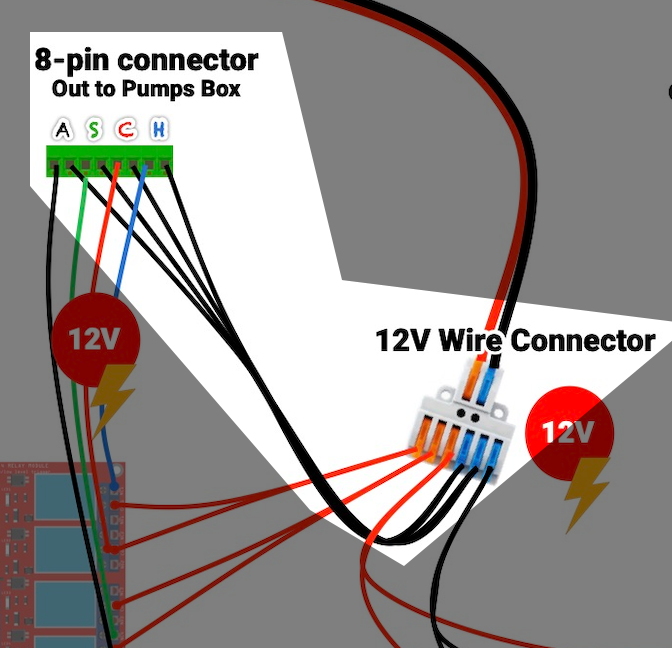
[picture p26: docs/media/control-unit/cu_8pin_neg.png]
Wire the negative Phoenix wires and connector
  

#### **Wiring the 4-channel Relay Board**

A relay is electronic on/off switch for the pumps etc. Each of the four relays on the 4-channel Relay Board has three screw terminals.

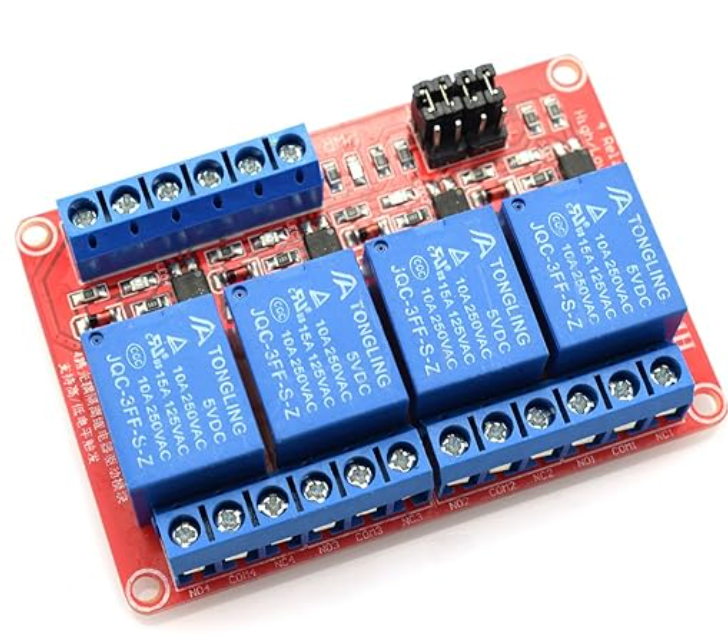
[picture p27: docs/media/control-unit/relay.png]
4-channel relay


For this project we will only use two of the terminals with each relay, the NO and the COM. The Normally Open (NO) means it keeps that part of the circuit open by default and no power flows. When the relay is activated, it physically connects the NO terminal to the Common (COM) terminal completing the circuit and then the power flows.
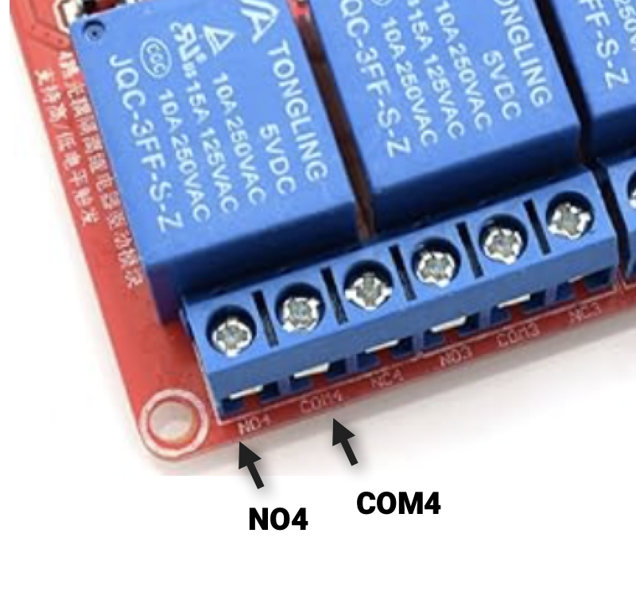
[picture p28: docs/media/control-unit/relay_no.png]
Wiring the positive 8-pin connector wires and connector


- **Wiring the NOs**
    - Take the 8-pin socket and insert the end of each of the 4" positive wires into the numbered NO terminals (NO1, NO2 etc) on the Relay Board. Tighten the terminals.
       - Black - NO4
       - Green - NO3
       - Red - NO2
       - Blue - NO1

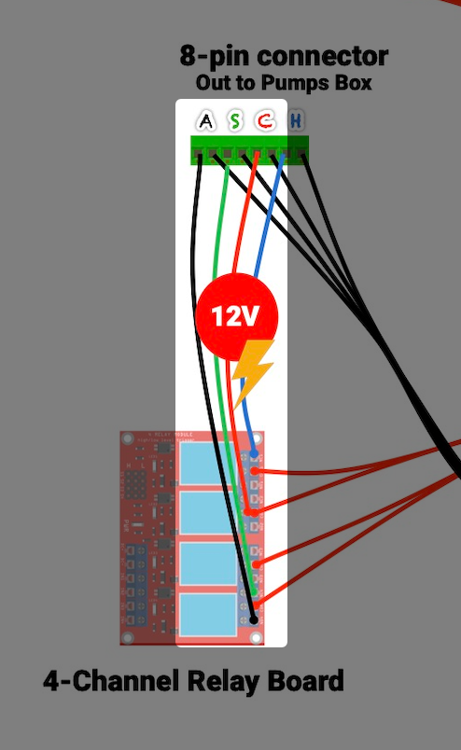
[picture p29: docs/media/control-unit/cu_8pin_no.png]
Wiring the NOs


- **Wiring the COMs**
   - Take the 4 red wires, insert one wire into each of the terminals labeled "COM" (common) tighten the terminals.

- **Connecting the Relay Board to the 12V Wire Connector**
 - Take the 12V wire connector, open the first two lever slots on the positive side of the connector (shown as the left side with red levers in our picture). Take the other end of the relay board's red COM wires, put two wires in each slot and close the slots.

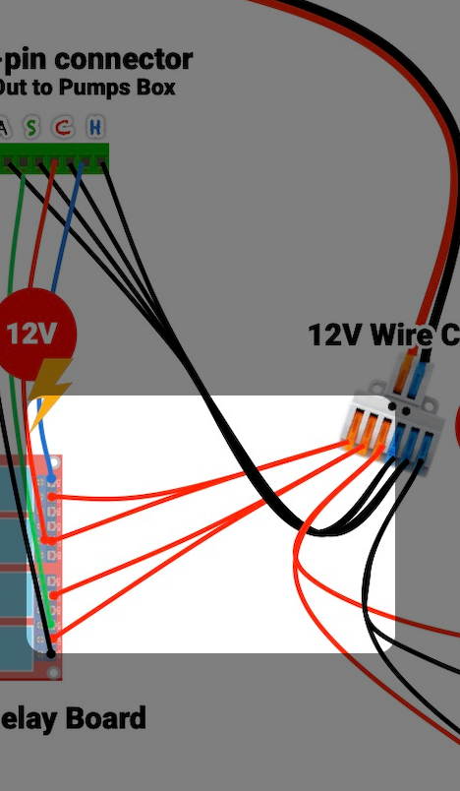
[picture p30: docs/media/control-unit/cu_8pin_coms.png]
Wiring relay to power


###  Arduino Shield wiring

In order to send 12V out to the peristaltic pumps, the Arduino CNC shield needs to be connected to the 12V Wiring Connector and the 12-pin connector.

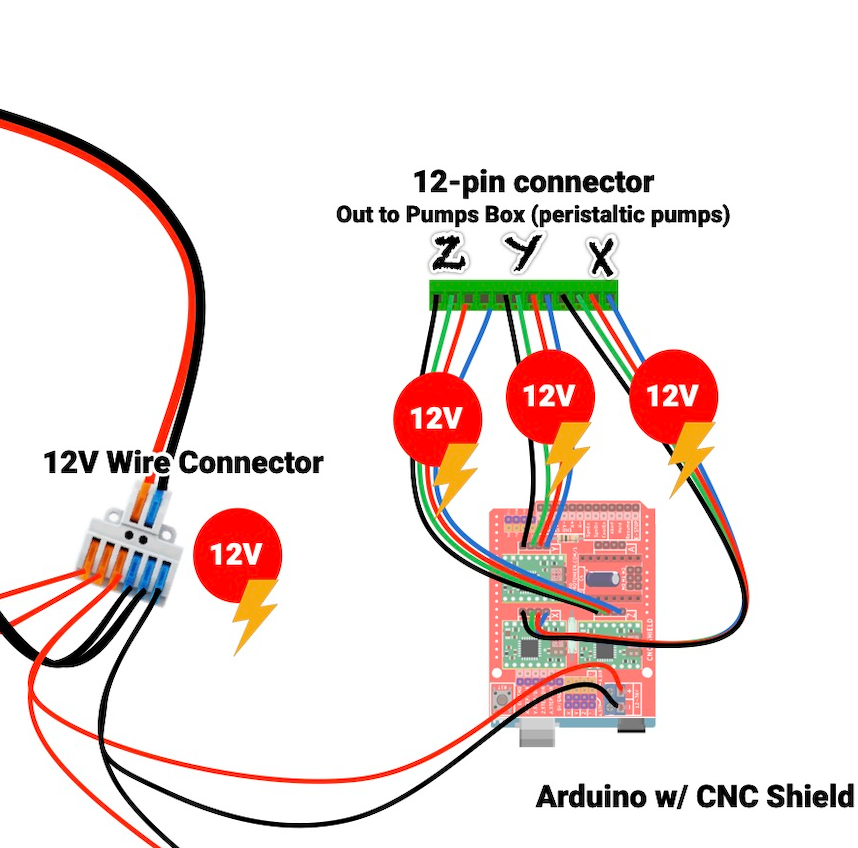
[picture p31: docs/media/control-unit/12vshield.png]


#### Wire Order

Please read and get comfortable with the wiring order explained on the [MicroLab Wiring](/docs/wiring.md) page. It's important to maintain the same wiring order throughout the project.

**12-pin connector - internal**.
The 12-pin connector passes 12V to the three peristaltic pumps. When looking at the pumps mounted to their box from left to right we'll call them X, Y and Z.

From inside the case the 12-pin connector wiring order will look like this:

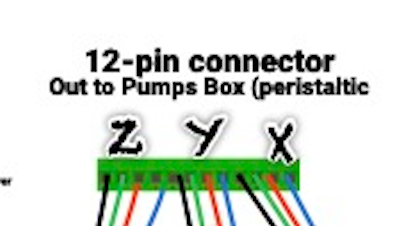
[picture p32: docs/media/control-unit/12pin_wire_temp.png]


#### Assembling the 12-pin Connector

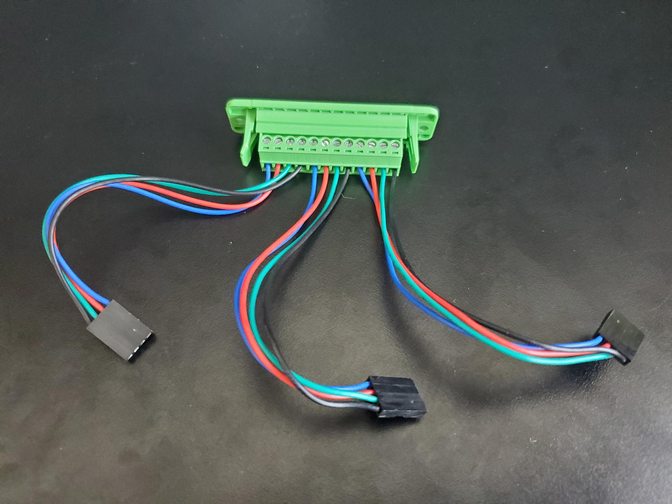
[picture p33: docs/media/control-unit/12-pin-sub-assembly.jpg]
12-pin sub-assembly parts


**Parts**

| Part ID      | Part Name     | Count | Notes |
| ------------- | ------------- |------| ----|
|SP-PC12|12-pin connector|1|
|SP-SMC|Stepper motor cables|6|

- Assembled Ardunio with the 4-wire stepper motor cables that were connected in the [Arduino Setup](#arduino) section.

**Assembly**

- Use a small screwdriver to open the screw terminals on the 12-pin connector.
- The stepper motor cables have a connector on one end and stripped wire on the other end. The wires need to be attached in order. Starting from the left take the Z wires and attach them in order:
  * Black  
  * Green
  * Blue
  * Red
- Next attach the Y and then X wires using the same order.

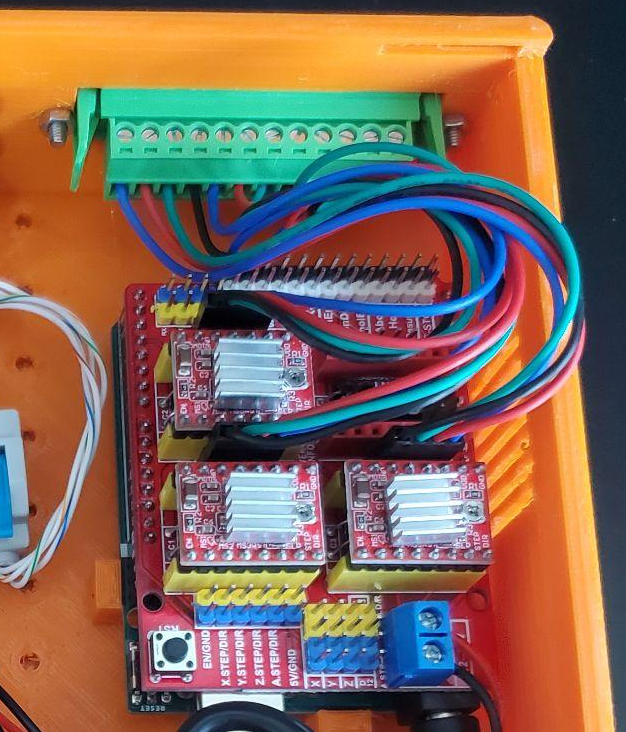
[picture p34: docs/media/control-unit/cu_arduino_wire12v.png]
12-pin wiring to Arduino


#### Wiring the 12V power on the CNC Shield

With CNC shield wired for the stepper motors, we will now wire it for the 12V power needed to drive those motors.

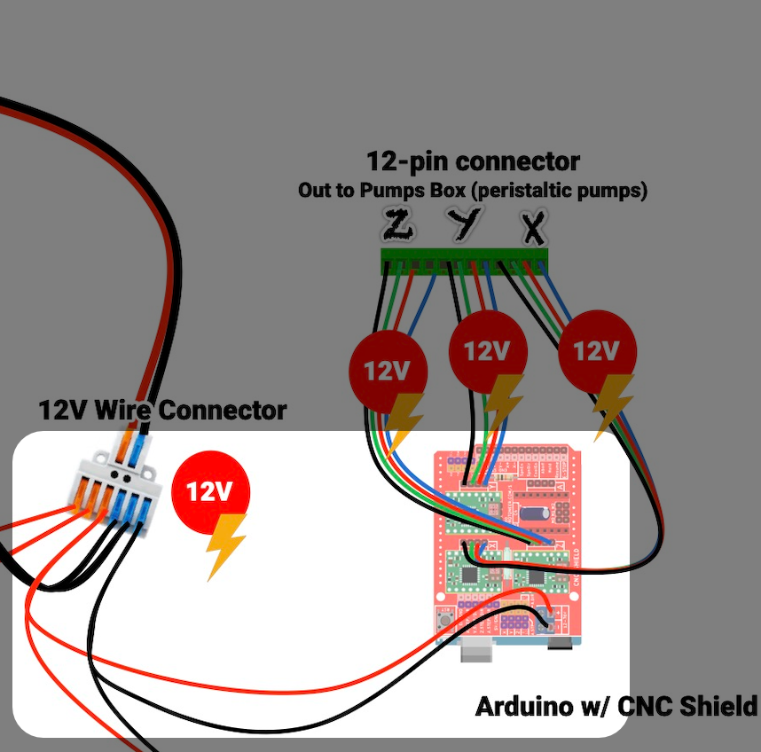
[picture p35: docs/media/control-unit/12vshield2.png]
Wiring 12V on CNC shield


**Parts**

| Part ID      | Part Name     | Count | Notes |
| ------------- | ------------- |------| ----|
|CU-WCL|Wire Connector (lever), 2-in-6-out|1| 12V Wire Connector
|SP-RBW|2-wire cable, red and black, 18 gauge |40ft roll| Used to make short wires

- Assembled Ardunio with the 4-wire stepper motor cables that were connected tin the [Arduino Setup](#arduino) section.

**Prepare Wires**

- Take the 2-wire cable (SP-RBW) and cut one 6" section
- Take the 6" section and separate the red and black wires
- Strip both ends on each of the wires (see [Skills Needed](#raspberry) for help with stripping wires).
    - Expect to remove 1/4" or more of the insulation. If the lever connector or screw terminal closes on the insulation the electricity won't pass through.

**Assembly**

- Wiring the Arduino's CNC Shield
    - Use a small screwdriver to open the screw terminals on CNC shield.
    - Insert the red wire into the positive (+) terminal on the CVC shield and tighten the terminal.
    - Insert the black wire into the negative (-) terminal on the CVC shield and tighten the terminal.
- Wiring the 12V Wire Connector (CU-WCL)
   - On the 12V Wire Connector there should be an empty slot on the positive (red) side. Open that lever, add the red wire and then close the lever.
   - On the 12V Wire Connector there should be an empty slot on the negative (black) side. Open that lever, add the black wire and then close the lever.

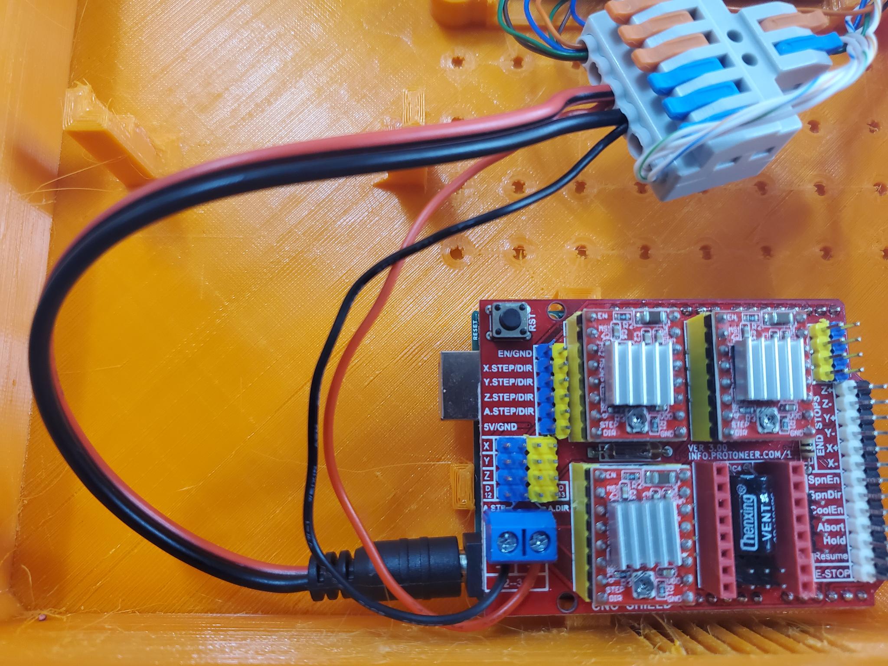
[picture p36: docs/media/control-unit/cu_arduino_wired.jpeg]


Take a moment to review and appreciate your work. This is the most fiddly part of the assembly. Nice job! 🎉

### Wiring the 12V to 5V Converter

The 12V Wire Connector passes the 12V power to the converter which, as the name says, will covert it into 5V power. The Converter sends the 5V power to the Raspberry Pi and 4-channel Relay Board as their power supplies.

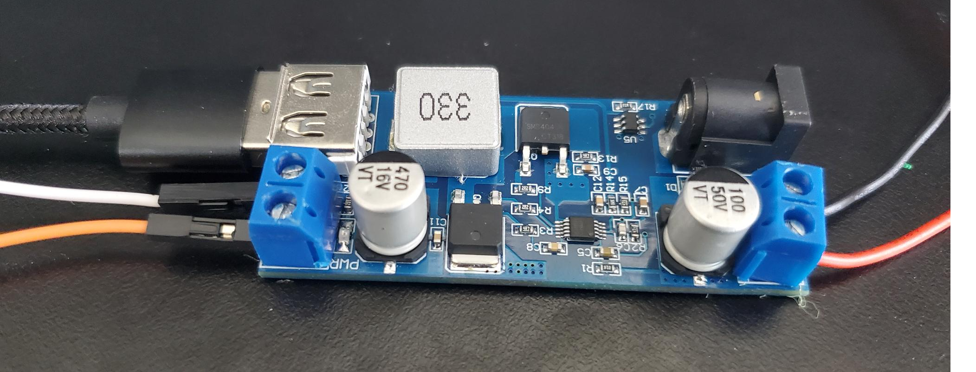
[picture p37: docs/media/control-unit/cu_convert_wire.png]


#### Parts

| Part ID      | Part Name     | Count | Notes |
| ------------- | ------------- |------| ----|
|CU-PLG|Barrel plug connectors|1| Male connector
|CU-WCL|Wire Connector (lever), 2-in-6-out|1| 12V Wire Connector
|CU-SDC|12V to 5V Converter |1 |

#### Assembly

- Take the 12V Wire Connector, locate the empty slot on the positive (red) side. Open the lever, insert the red wire and then close the lever.
- On the 12V Wire Connector locate the empty slot on the negative (black) side. Open that lever, insert the black wire and then close the lever.
- Plug the male barrel plug connector into the 12V to 5V converter module.

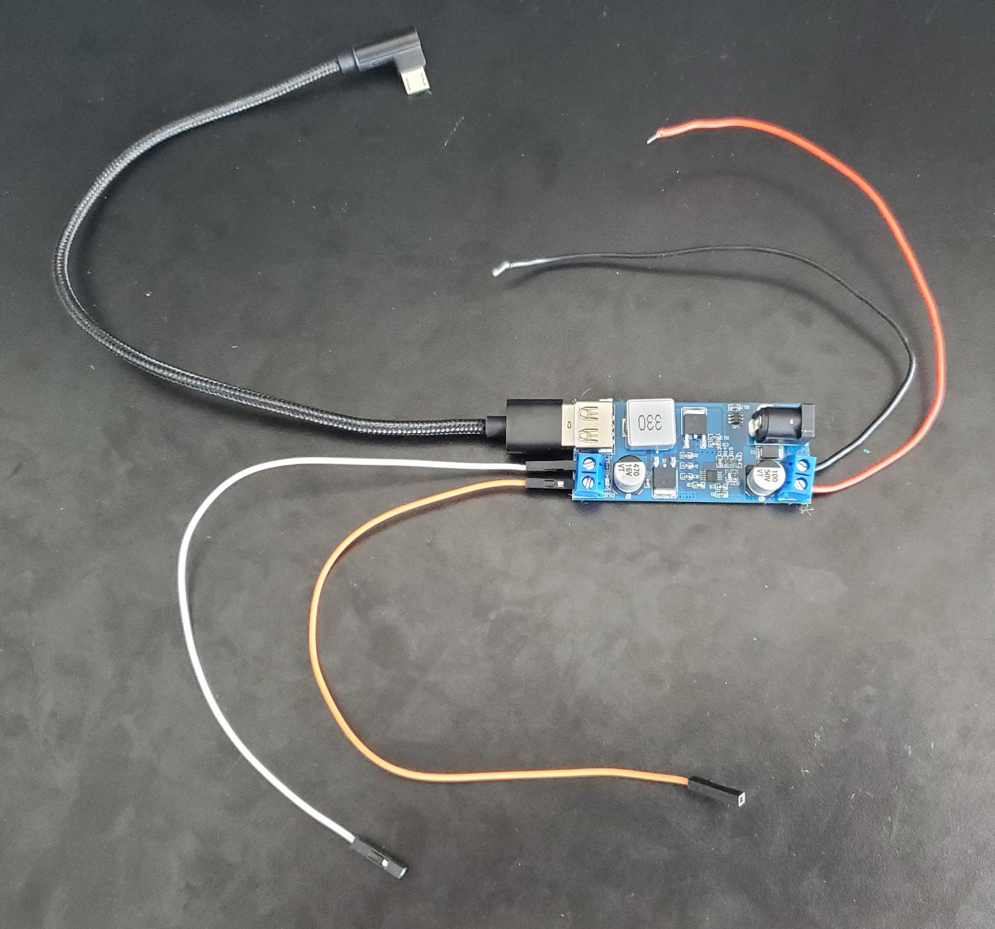
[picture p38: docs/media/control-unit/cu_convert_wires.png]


## Wiring 5V and Signals on the Relay Board

The rest of the wiring runs some combination of lower voltage power, signals and data between components.

The Raspberry Pi, 4-Channel Relay Board and the Arduino all run using 5V power. The 12V to 5V Converter supplies that power to the Raspberry Pi and 4-Channel Relay Board so they can work.

The Raspberry Pi sends 5V power (and data) out to the Ardunio and the 2 mounted USB ports through USB cables.  

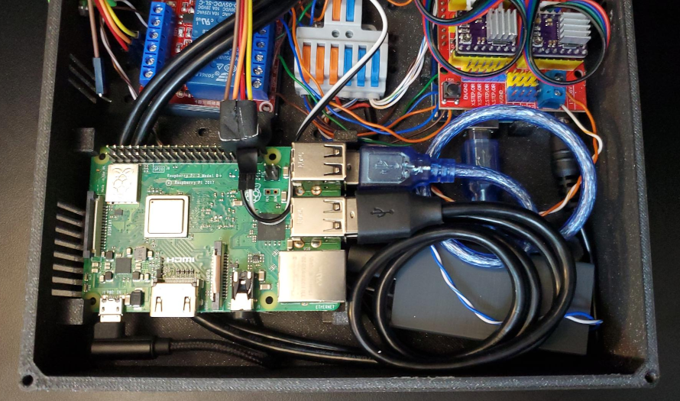
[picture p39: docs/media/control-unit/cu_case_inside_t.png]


#### Relay Board Layout

We've already wired the 4 relays on the "12V side" of the 4-Channel Relay Board. Now we are going to wire the other half of the board, you will see a small terminal block with 6 screw terminals.

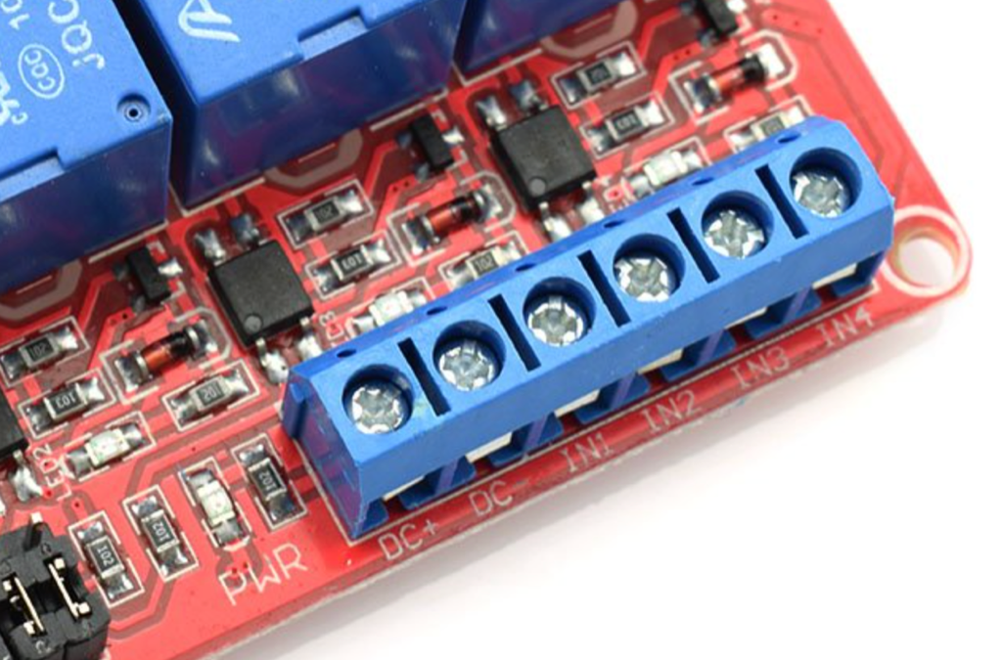
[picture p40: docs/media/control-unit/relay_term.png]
Relay terminals


These six terminals are:
  - **(DC+) terminal**: 5V power positive (+) to run Relay Board
  - **(DC-) terminal**: 5V power negative (-) to run Relay Board
  - **(IN1) terminal**: Signals Relay Board to turn on/off Relay 1 (Blue/Heat)
  - **(IN2) terminal**: Signals Relay Board to turn on/off Relay 2 (Red/Cool)
  - **(IN3) terminal**: Signals Relay Board to turn on/off Relay 3 (Green/Stir)
  - **(IN4) terminal**: Signals Relay Board to turn on/off Relay 4 (Black/Accessory)

**Parts**

| Part ID      | Part Name     | Count | Notes |
| ------------- | ------------- |------| ----|
|CU-CNC|12V to 5V Converter |1
|CU-WCL|Wire Connector (lever), 2-in-6-out|1
|SP-RBW|2-wire cable, red and black, 18 gauge |40ft roll| Used to make short wires | 1
|CU-RAH| Right angle header row
CU-JMP|Breadboard Jumper Wires - male-female|4| For consistency we used black, green, red, and blue
|SP-ETN|Electrical tape, narrow|1 roll
|CU-RCP|Relay case|1

**Prepare Wires**

  - Take the 2-wire cable (SP-RBW) and cut one 6" section
    - Take the 6" section and separate the red and black wires
    - Strip both ends on each of the wires (see [Skills Needed](#raspberry) for help with stripping wires).
  - Prep the headers. Take the right angle header row and use the wire cutters to cut four 1-pin pieces.
     - If not using the 90 degree header pins, then use needle nose pilers to gently bend each of the male headers on the Jumper wires to a 90 degree angle.

**Assembly**

- **Adding wires.** Use a small screwdriver to open the 6 screw terminals on Relay Board. Then insert the appropriate wire to the terminal and then tighten the screw terminal.
  - **(DC+) terminal**: attach the 6" red wire
  - **(DC-) terminal**: attach the 6" black wire
  - **(IN1) terminal**: attach the right-angle header pin and then plug in the male end of the blue (Heat) jumper wire
  - **(IN2) terminal**: attach the right-angle header pin and then plug in the male end of the red (Cool) jumper wire
  - **(IN3) terminal**: attach the right-angle header pin and then plug in the green (Stir) jumper wire
  - **(IN4) terminal**: attach the right-angle header pin and then plug in the black (Accessory) jumper wire
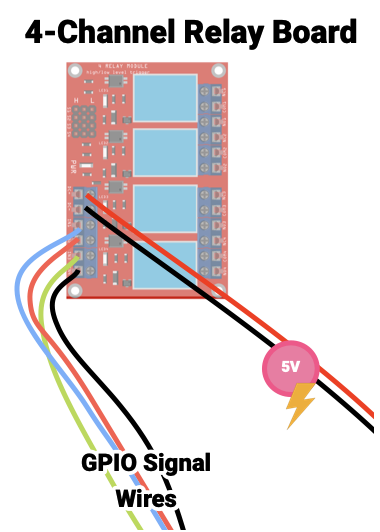
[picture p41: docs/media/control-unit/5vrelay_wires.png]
  

- **Relay Board cleanup.** To conserve space and prevent short circuits, we recommend using flush cutters to trim pins sticking out on the underside of the board. Then use electrical tape to cover the bottom of the board.
- **Relay Board Case**. The prepped Relay Board should fit in the Relay Board Case
   - For more information about the 3D printed parts check the [How to build & use the MicroLab and MicroLab Suite](docs/index.md) page.
- **Cable Management.** Gently bend all wires on both sides of the relay up and wrap them with narrow strips of electrical tape.
 - Tape prevents shorts and helps keep the wires from being damaged as you arrange components in the case.

Now we will mount the connectors to the Control Unit Case.

## Mounting Components in the Case

To connect the Control Unit to the outside world we will mount the connectors to the case:

* 12-pin connector (out to peristaltic pumps)
* 8-pin connector (out to circulating pumps, stir rod, and accessory port)
* 2-pin connector (out to heating coil)
* USB ports (2) (out to thermistor)
* Barrel port (12V in)

#### **Parts**

|Part ID      | Part Name     | Count | Notes |
| ------------- | ------------- |------| ----|
|CU-CBC|Control Case (Printed)|1
|CU-WCL|Wire Connector (lever), 2-in-6-out|1
SP-PC12| 12-pin connector|1| Mount plate
SP-PC8|	8-pin connector| 1 | Mount plate
SP-PC2|	2-pin connector|1 | Mount plate
CU-PLG|	Barrel plug connectors | Female barrel plug connector
CU-USB|	Mountable USB cables|2 |
SP-QDC|	Quick-disconnect connectors|2 |
SP-M3S-16|16 mm M3 screws with nuts| 6 |

- 12V Circuit
  - 4-channel relay, wired to the 8-pin socket
  - Arduino w/ CNC shield, wired to the 12-pin socket
  - 12V Wired Connector
  - 12V to 5V Converter

### **Place the 12V Circuit**

- Orient the case so the 8-pin and 12-pin openings are at top when looking down at the case.
- Across the top half of the case gently place from the left (see picture):
   - 4-channel Relay Board
   - 12V Wired Connector
   - Arduino w/ CNC shield
- In the bottom right of the case, place the 12V to 5V Converter.

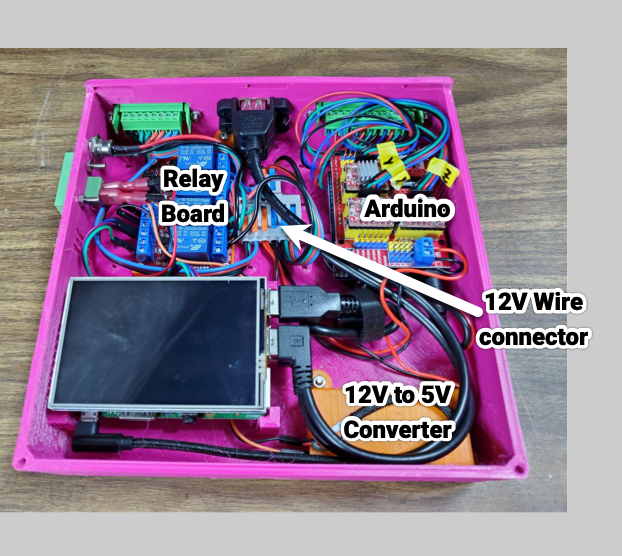
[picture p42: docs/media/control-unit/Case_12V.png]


**BE NOT AFRAID: This image shows the v0.6.0 version of the MicroLab as do a few others. There are some small differences but the wiring and layout are very much the same.

### Installing the 12/8/2-pin connectors

Panel-mounted components installed

**NOTE** These parts can be hard to come by and are not essential. They're just very convenient wire connectors. Any 8 and 12-pin connector will do a similar job, just take care to secure the cabling so it doesn't yank on the electronics inside the Control Unit. The 2-pin connector is not required if you are using an off-the-shelf heat source like a deep fryer.

- **Install the 12-pin mount plate.** Orient the mount plate and use 2 M3 screws to install it on the outside of the case.
- **Connect the 12-pin socket** Take the 12-pin socket attached to the Arduino and connect it to the back of the 12-pin mounting plate.
- **Install the 8-pin mount plate.** Orient the mount plate and use 2 M3 screws to install it on the outside of the case.
- **Connect the 8-pin socket** Take the 8-pin socket attached to the Relay Board and connect it to the back of the 8-pin mounting plate.
- **Install the 2-pin assembly.** Orient the mount plate and use 2 M3 screws to install it on the outside of the case (left-side). We won't connect the 2-pin socket in this step.

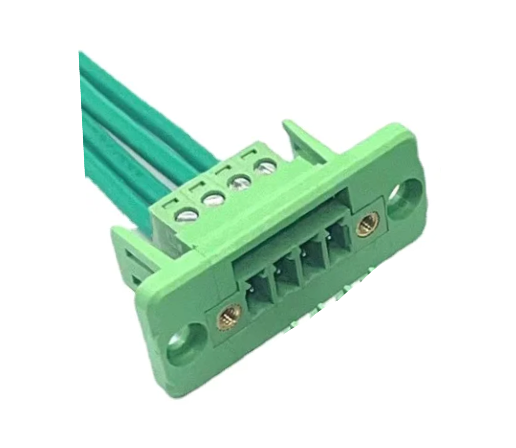
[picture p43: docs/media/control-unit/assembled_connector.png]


### Installing the Ports

**Install the Barrel Port.** Insert the female barrel plug connector in the circular hole on the left side of the case and attach with the matching nut.

**Install the USB Ports.** Mount the USB ports to the case. The USB case holes are between the 8-pin and 12-pin connectors. They should have come with their own screws. We recommend installing them with the plastic rectangle at the top, but feel free to be a chaos muppet about it if that's your jam.

## Installing the Components in the Control Unit Case

Now we can connect some last wires and install all the components in the case:

* 4-channel Relay Board
* Arduino w/ CNC shield
* 12V Wire Connector
* Raspberry Pi

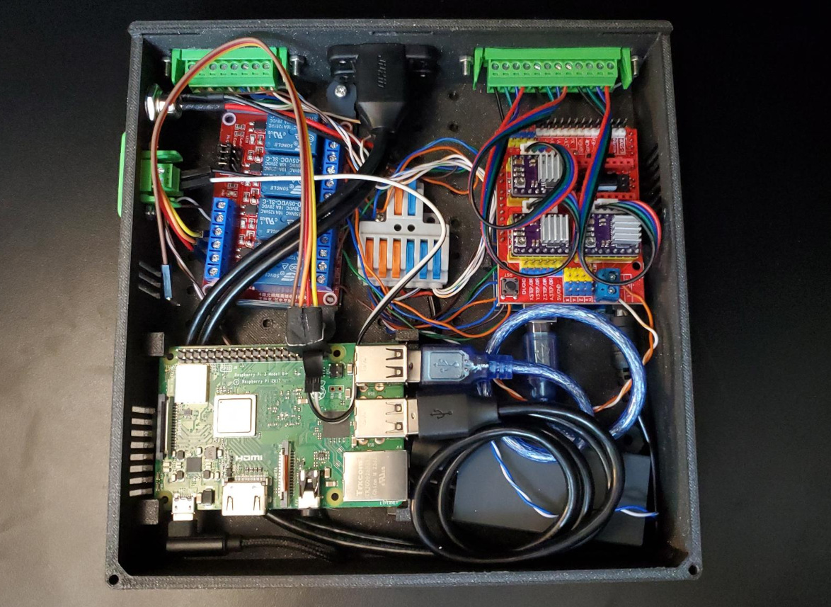
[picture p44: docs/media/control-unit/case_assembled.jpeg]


#### **Parts**

- Case w/ connectors installed
- 12V Circuit
  - 4-channel relay, wired to the 8-pin socket
  - Arduino w/ CNC shield, wired to the 12-pin socket
  - 12V Wired Connector
  - 12V to 5V Converter
- Converter case
- Barrel plug connector
- 20 mm M3 screws with nuts (2)
- Micro USB Cable, right angle, Power cable for Raspberry Pi
- USB A/B cable for Raspberry Pi to Arduino

### Installing the 12V to 5V Converter

**Parts:**

- 12V to 5V Converter
- Converter case
- Micro USB cable for Raspberry Pi
- 4-channel Relay Board

**Assembly**
- **Place Converter in its converter case.** Orient the 12Vto 5V converter and slide it into the Converter Case (shows as orange case in picture).
- **Add Power for the Raspberry Pi.** Plug the USB cable for the Raspberry Pi into the USB port on the converter.
- **Add Power for the Relay Board.** Insert the DC+ red wire and DC- black wire into the screw terminal on the Relay Board.
- **Install Converter in Control Unit Case.** Position the Converter in the lower right corner of the flat case. The circular mounting tab on the Converter case should line up with a hole in floor of the Control Unit case. Use an M3 screw to secure the Converter case to the floor.

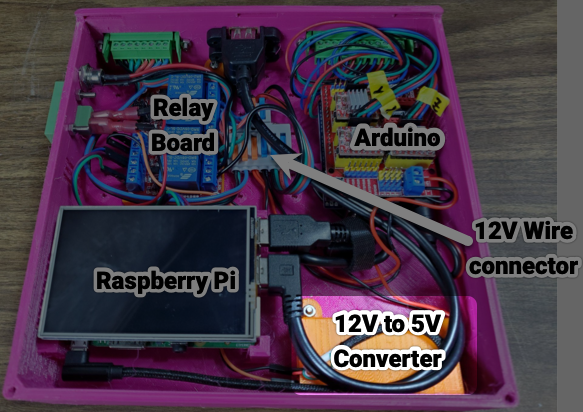
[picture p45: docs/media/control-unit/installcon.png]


### Installing the 4-channel Relay Board

**Parts:**

- 4-channel Relay Board
- Relay Board case (3D printed)
- 12mm M3 screws (1)

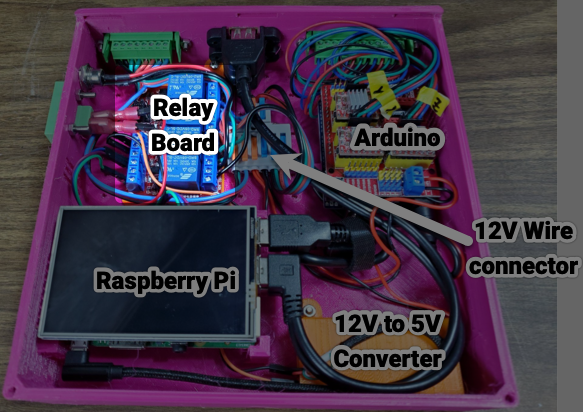
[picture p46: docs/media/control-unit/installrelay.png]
Relay Board installed in the case

<BR>
<BR>

- **Install Relay Board in Control Unit Case.** Position the Relay Board in the upper left corner of the flat case. The circular mounting tab on the Relay Board case should line up with a hole in the floor of the Control Unit case. Use an M3 screw to secure the Relay Board case to the floor.
- **Cable Management** You may need to unplug the cable from the converter. From the Relay Board run the cable to the bottom of the case and then run it to the right to tuck the cable into the case.

### Installing the Arduino

#### **Parts**

- Arduino w/ CNC shield
- USB A-to-B cable

#### **Assembly** 

- **Install Arduino in Control Unit Case.** Insert the Arduino w/ CNC shield into its spot in the upper right of the case with its USB port facing the center. It should slot into the supports snugly when pushed toward the right side of the case.
- **Add power cable for the Arduino.** Plug the USB B side of the A-B cable into the USB port on the Arduino
- **Check your work** Verify the red and black wires are secured to the (+) and (-) terminals on the Arduino shield.

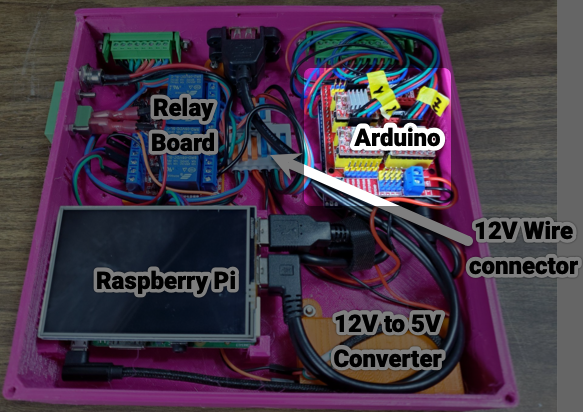
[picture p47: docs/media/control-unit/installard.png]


### Installing the 12V Wire Connector

- Female barrel plug connector, attached to case
- 12V Wire Connector
- 12mm M3 screws (2)

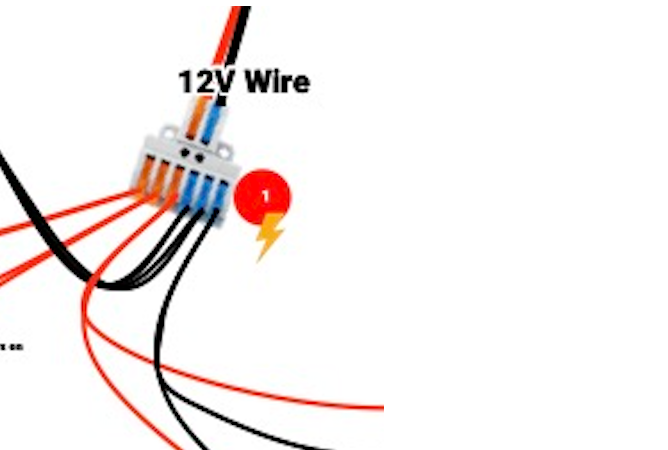
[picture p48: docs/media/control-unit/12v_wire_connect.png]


### **Assembly**

**Add "12V power in" wires to the Wire Connector.** Take the two wires on the installed female barrel plug connector and connect the red wire (positive) to the red (positive) slot on the 2-in side of the Wire Connector. Take the black wire (negative) and insert it to the blue (negative) slot on the 2-in side of the Wire Connector.   

**Install 12V Wire Connector in Case.** Position the 12V Wire Connector in the case and use 2two 12mm M3 screws to screw the connector to the floor of the case.

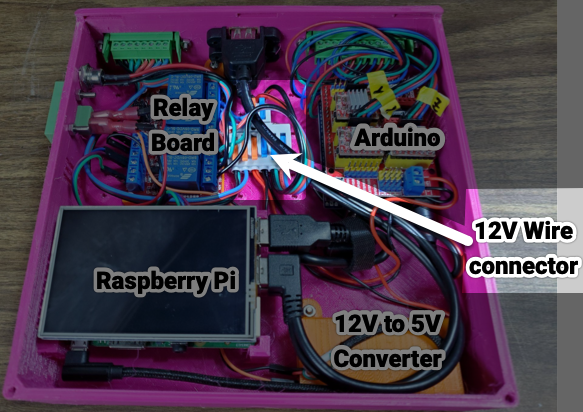
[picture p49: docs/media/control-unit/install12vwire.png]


<BR><BR>

### Installing the Raspberry Pi

- Raspberry Pi
- Mounted USB Cables
- Micro A/B USB cable attached to the Arduino

### **Assembly**

#### Attach USB Cables and Install in Case
- Plug the Arduino's USB cable into the Raspberry Pi.
- Plug the USB cables into the Raspberry Pi.
- Remove the touchscreen and set aside.
- Insert the Raspberry Pi into its case supports, starting with the left side of the board, and keeping the USB ports toward the center. The supports have catches that should hold the board snugly in place.

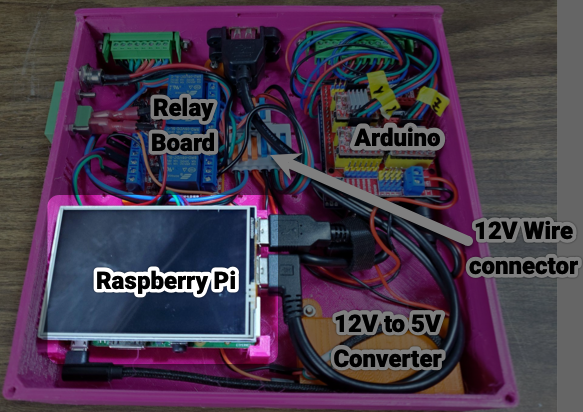
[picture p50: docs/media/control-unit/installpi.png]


#### Connect the Signal wires to the GPIO pins

The wires we attach to the header GPIO pins let the Raspberry Pi control the relays on the Relay Board as well as the heater coil.

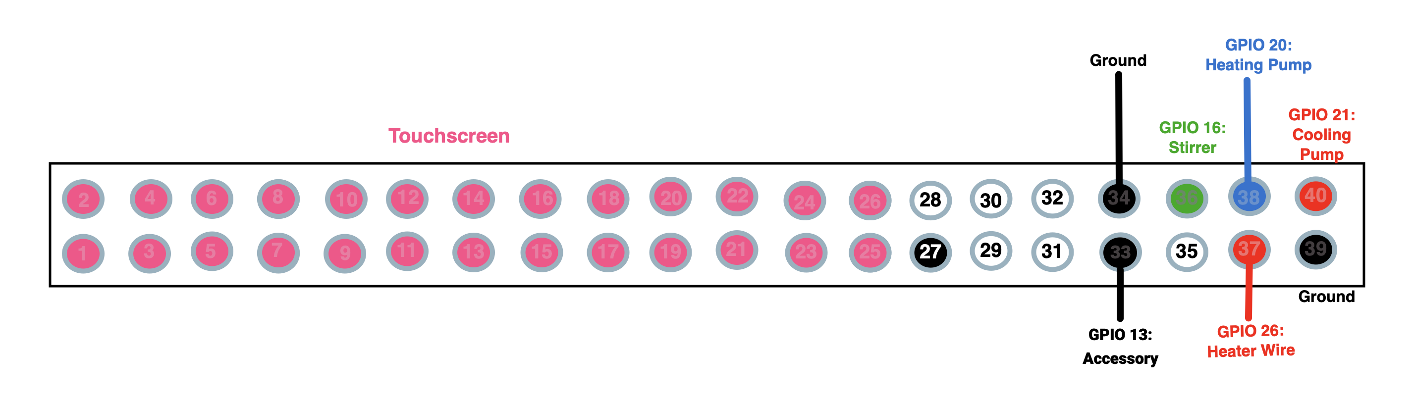
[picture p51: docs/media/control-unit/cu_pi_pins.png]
GPIO pins


**Tools:**

- Wire cutters
- 4-channel Relay Board

**Parts:**

- Raspberry Pi with touchscreen off
- 4-channel Relay Board
- 2-pin connector, wired
- Right angle header row, female-male

**Assembly:**

- **Add headers to the Raspberry Pi.** Take the right angle header row and use the wire cutters to cut two 4-pin pieces. Place them at the end of the pin block, push one on to the 34, 36, 38, 40 pins and the other on the 33, 35, 37, 39 pins.
- **Connecting the Relay Board Wires**
  - Take the IN1 Blue (Heat) wire and attach the female header to Pin 38 (GPIO 20)
  - IN2 Red (Cool) and attach the female header to Pin 40 (GPIO 21)
  - IN3 Green (Stir) and attach the female header to Pin 36 (GPIO 16)
  - IN 4 Black (Accessory) and attach the female header to Pin 33 (GPIO 13) <BR>
  External control wires
- **Connecting the Heater Coil Wired**
  - Take the 2-pin connector and attach wire ends
    - Black wire female header to Pin 34 (Ground)
    - Red wire female header to Pin 37 (GPIO 26)
- **Cable Management**
   * Tape the GPIO pins together to secure them. See picture.
   * Carefully tuck the wires into the case so that they will not obstruct the lid.

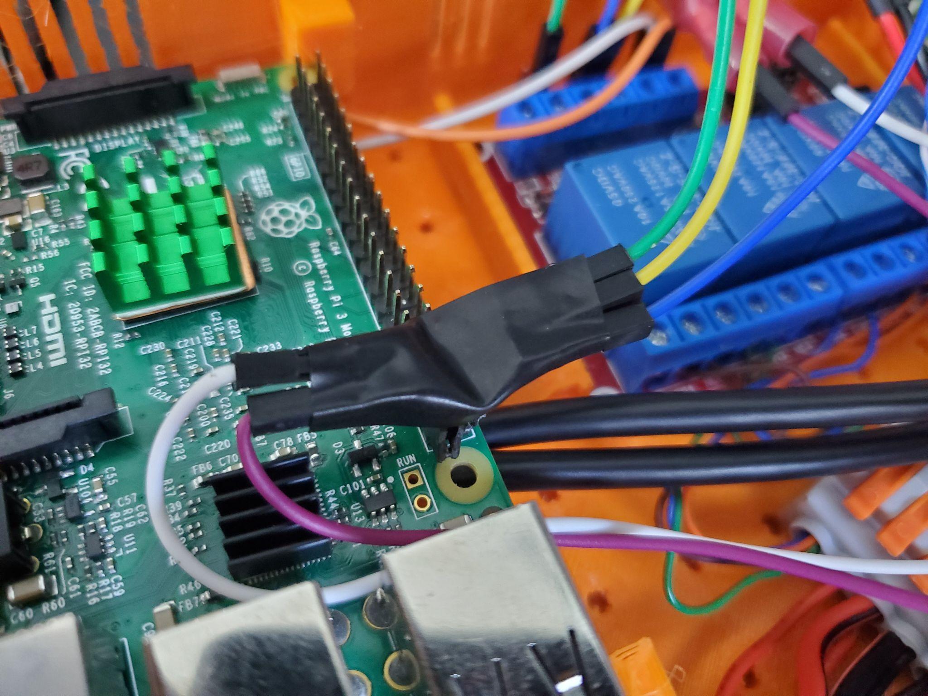
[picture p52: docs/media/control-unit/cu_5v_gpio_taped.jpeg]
GPIO pins
 <BR><BR>

- **Attach touchscreen.** 
   * Attach the touchscreen to the Control Unit lid with the screws it came with.
   * Connect the ribbon cable to the screen and to the display port on the Pi.

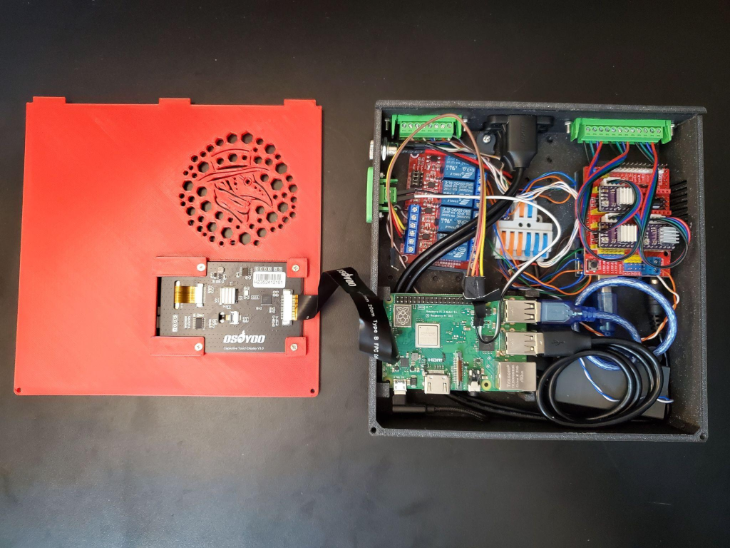
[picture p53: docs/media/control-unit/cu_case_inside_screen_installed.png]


## Final Assembly

Before you close the case, you probably want to test that everything is wired correctly. We **highly** recommend testing all the functionality of the MicroLab using the Test Recipe. Of course, if something doesn't work right or stops working in the future, you can always open it back up again.

**Parts:**
- Control Unit lid
- 2 M3 screws, 16mm

**Assembly:**

- Place the lid on top of the Control Unit case with the tabs in the tab slots.
- Check to see that the display cable isn't getting too bent or twisted as the lid closes.
- Align the screw holes on each and secure the lid in place using the 16mm screws.

🥳 YAY! ✨🦄✨ You did it! 💖

Control Unit

## One Last Thing: Making MicroLab Cables

To connect your newly assembled Control Unit to the Pumps Unit, you will use a pair of cables: 8-wire and 12-wire. Savvy readers will notice that this corresponds with the 8-pin and 12-pin connectors.

#### **Wire Order** 

**Important Note: The wire order here is different than in other sections.**

Please read and get comfortable with the wiring order explained on the [MicroLab Wiring](/docs/wiring.md) page. It's important to maintain the same wiring order throughout the project.

**8-pin cable**.

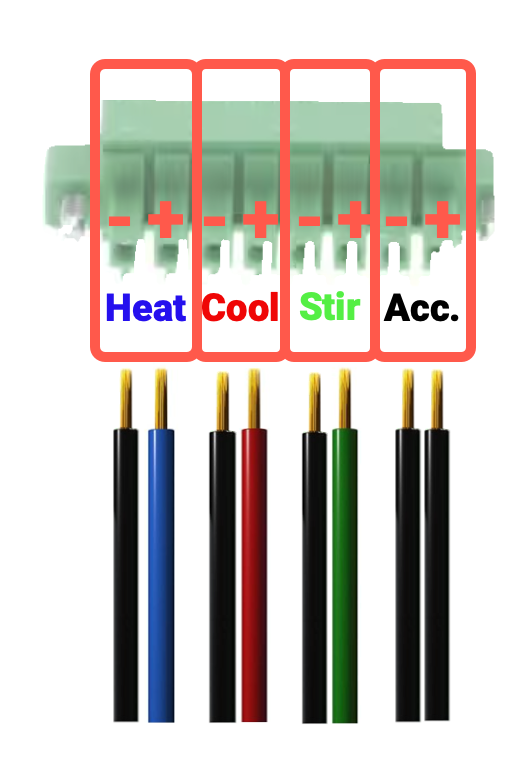
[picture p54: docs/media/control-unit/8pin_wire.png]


**12-pin cable**.
From left to right, repeat this wire order 3 times:
* Blue
* Red
* Green
* Black

Note: This assumes you used the 4-wire cable recommended in the parts list. If you brought your own or are using ethernet cables, just make sure that the wiring is consistent on either end.

Cable order

#### **Parts**

- 4-wire cable, into 5 2.5-foot+ lengths
   * You can also use ethernet cable here
- 8-pin connectors, plug (2)
- 12-pin connectors, plug (2)
- Split wire wraps (slightly shorter than the cables)

Cable parts
Assembled cables

**Prepare Wires**

- Take the 4-wire cable and cut into five 2.5+ foot sections
- Take the 2.5+ foot sections and strip the wires on both ends  (see [Skills Needed](#raspberry) for help with stripping wires).

**Assembly:**

**Important Note: The wire order here is different than in other sections, be sure you have the correct order.**

**Making the 8-pin cable**
 * Take one of the 8-pin connector plugs and two of the 2.5 foot sections.
 * From the back of the plug, attach the wires in order. For the plug side of the connector, you use the small orange push buttons to open the terminal, insert the wire and then release the button to close the terminal.
 * Take the second 8-pin connector plug and connect the wires. Be sure that the wire order is consistent at both ends of the cable.
 * Wrap the assembled 8-pin cable in the wire wrap

**Making the 12-pin cable**
* Take one of the 12-pin connector plugs and two of the 2.5 foot sections.
* From the back of the plug, attach the wires in order. For the plug side of the connector, you use the small orange push buttons to open the terminal, insert the wire and then release the button to close the terminal.
* Take the second 8-pin connector plug and connect the wires. Be sure that the wire order is consistent at both ends of the cable.
* Wrap the assembled 8-pin cable in the wire wrap

Cable ends

## Wrapping up

This concludes the assembly instructions for the Control Unit. Next up: [Building the Heating and Cooling Units](/docs/assembly-temperature-exchangers-unit.md)

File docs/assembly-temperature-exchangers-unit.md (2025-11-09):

# Heating and Cooling Units Assembly

The Heating Unit and Cooling Units are supporting components of the MicroLab that heat or cool the fluids that circulate in the Reactor Core.

Temp Tubing

## 🚨 UNDER ACTIVE DEVELOPMENT🚨

Please note that this part of the project is under active development.
While these instructions show jars for the heat source and heat sink, these can be limited and impractical for many applications.
Our development team is exploring additional options like:
- A [mini deep fryer](https://www.amazon.com/dp/B09HW3GFKP?th=1) full of propylene glycol as a heat source.
- A [mini chest freezer](https://www.homedepot.com/p/COWSAR-20-67-in-W-1-8-Cubic-Feet-Manual-Defrost-Garage-Ready-Chest-Freezer-with-Adjustable-Temperature-Controls-in-Black-SZHD-D5850-BLACK/330363273) as a heat sink.
- Even a cooler full of ice would be better than a jar.
- You can also insulate the tubing and reactor core for added efficiency.

We will update with more details as part of the next release.

## Skills Needed

* Bending copper tubing

## Tools Needed

* Copper tube jig - for bending the copper without pinching it (optional but recommended).
    - Jig options includes
      - a cylinder with a smaller diameter than the jar or a medium-to-large dowel/tube
      - the Reactor Core manifold, which is approximately the correct size. We opened [an issue about this](https://github.com/FourThievesVinegar/solderless-microlab/issues/136)
* Tube cutters - very helpful for neatly cutting the copper tubing without crushing it

## Parts

**Purchased parts info.** For more information on purchased parts, check the [MicroLab Parts List](microlab-parts-list.xslx).

**Printer parts info.** Parts listed as printed, like "CU-CB Control Case (Printed)", are 3D printed, check the [3D Printed Parts section ](docs/index.md#3d) of the "How to build the MicroLab" page.

| Part ID      | Part Name     | Count | Notes |
| ------------- | ------------- |------| ----|  
|||
TC-PMP|Circulating pump|2
TC-CTB|10` Copper tubing 1/4" OD x 3/16" ID|2
TC-STB|Silicone tubing 8mm OD x 5mm ID|1
TC-TCT|	Copper tube cutter tool|1
TC-CTJ|	Copper tube jig	|1

### Auxiliary heat sources and sinks

As mentioned above, we are looking for optimal head sources and sinks. Consider ice baths and deep fryers with operational temperatures below 188.2 °C / 370.8 °F (the boiling point of propylene glycol).

## Assembly

Temperature Units fully assembled

### Heat Exchanger

This component heats and stores hot water, or other liquids, which are then used to heat the Reactor Core.

* **Bending the tubing.** Gently bend the copper tubing into a helix that will fit in the jar, be sure to leave space for the heating coil.
 - Tips
    - More is better, the more copper tubing you can fit, the more heat will be exchanged.
    - It is OK (good even!) if the copper tubing and heating coils touch.
    - Take care when bending, copper tubing kinks easily, reducing or blocking the flow of the liquid.
    - You can support the tube using a long spring around  it or fill the tube with salt or sand to support it from the inside.

Put this in something hot like a deep fryer with operational temperatures below 188.2 °C / 370.8 °F (the boiling point of propylene glycol)

Temp Tubing

### Cooling Unit

This component holds ice water or another cold substance to cool the reactor core.

* **Bending the tubing.** Gently bend the copper tubing into a helix that will fit in the jar.
 - Tips
    - More is better, the more copper tubing you can fit, the more heat will be exchanged.
    - Take care when bending, copper tubing kinks easily, reducing or blocking the flow of the liquid.
    - You can support the tube using a long spring around it or fill the tube with salt or sand to support it from the inside.

Put this in something very cold like an ice bath or a block of ice in a mini chest freezer. We are exploring the best methods for this.

### MicroLab Connector Tubing

Both the Heating and Cooling Units will need two pieces 16 inch tubing and 1 piece of 8 inch tubing to connect them to MicroLab during operation. You may want to cut these tubes shorter (or longer) depending on your setup.

* Take the silicone tubing (TC-ST7) and cut four pieces to be 16 inches (16") long.
* Cut two pieces to be 8 inches (8") long.
* These lengths have worked for us so far. You may find different lengths works better for you and we'd love to hear what works.
* You can wrap the tubes in insulating material to increase efficiency. We are looking for affordable options here and will update the docs when we settle on the best / easiest / most available method. For now, you can buy commercial stuff that fits around the silicone tubes or even use silicone tubes with an interal diameter slightly larger than the external diameter of the silicone tubing (TC-ST7).

This concludes the assembly instructions for the Heating and Cooling Units. Next up: [Building the Reactor Unit](/docs/assembly-reactor-unit.md)

Temp Tubing

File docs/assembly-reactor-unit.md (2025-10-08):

# MicroLab Reactor Unit Assembly

The Reactor Unit is where the action happens, it is made up of the pumps, pump case, reactor core and reactor unit stand.

- [Assembling the Pumps Box](#pumps)
- [Assembling the Reactor Core](#core)
- [Assembling the Reactor Unit](#unit)

Reactor unit fully assembled

## Skills Needed

- Wire stripping - one example [video](https://www.youtube.com/watch?v=N__OLJvq2HE)

## Parts

**Purchased parts info.** For more information on purchased parts, check the [MicroLab Parts List](microlab-parts-list.xslx).

**Printer parts info.** Parts listed as printed, like "CU-CB Control Case (Printed)", are 3D printed, check the [3D Printed Parts section ](docs/index.md#3d) of the "How to build the MicroLab" page.

| Part ID | Part Name                                    | Count | Notes                                                                                                     |
| ------- | -------------------------------------------- | ----- | --------------------------------------------------------------------------------------------------------- |
|         |                                              |
| RU-SRM  | Stir rod motor                               | 1     |
| RU-STR  | Stir rod                                     | 1     |
| RU-SRC  | Stir rod coupling                            |
| RU-LID  | Reactor Core manifold (Printed)               | 1     | 
| RU-RJF  | Jar Flanges (Printed)                        | 2     |
| RU-COR  | 250ml GL45 Borosilicate Glass Bottle             | 1     |
| RU-OUT  | 32oz wide mouth mason jar for outer jacket   | 1     |
| RU-SDH  | Reactor stand - H (Printed)                  | 1     |
| RU-SDH  | Reactor stand - A (Printed)                  | 1     |
| RU-SDH  | Reactor stand - ¢ (Printed)                  | 1     |
| RU-SDH  | Reactor stand - K (Printed)                  | 1     |
| RU-TMP  | Thermistor                                   | 1     |
| RU-PPM  | Peristaltic pumps with stepper motors        | 3     | [Or printable syringe pumps](https://github.com/FourThievesVinegar/microlab-parts/tree/main/syringe-pump) |
| SP-SMC  | Stepper motor cables                         | 3     | 6-pin end for motors                                                                                      |
| RU-SYR  | Syringes                                     | 3     |
| RU-PUB  | Pumps box (Printed)                          | 1     |
| RU-PUL  | Pumps lid (Printed)                          | 1     |
| RU-SUP  | Wire coat hanger                             | 1     |
| TC-PMP  | Circulating pump                             | 2     |
| SP-PC12 | 12-pin connector, panel-mount screw terminal | 1     |
| SP-PC8  | 8-pin connector, panel-mount screw terminal  | 1     |
| CU-PLG  | Barrel plug connectors, 5.5mm x 2.1mm        | 2     | female                                                                                                    |

## Assembling the Pumps Box

The Pumps Box has 3 Peristaltic pumps w/ stepper motors on the front that inject reagents into the Reactor Core and the 2 circulating pumps on the sides that move hot and cold fluids to control the Reactor Core's temperature. It also has plugs on the front for the stirring motor and an accessory port that can be used to power accessories like a light.

Pumps Box Front showing three peristaltic pumps and two female barrel connectors on the front of a 7 inch by 7 inch 3D printed box

### Tools required

- Small screwdrivers for M3 screws
- Wire cutters and strippers

### Parts

- 3 Peristaltic pumps w/ stepper motors (RU-PPM)
- 2 Circulating pumps (TC-PMP)
- 12-pin connector
- 8-pin connector
- 2 barrel plug connectors, female (5.5mm x 2.1mm)
- 3 stepper motor cables, the 6 pin end that connects to the stepper motors
- 20 M3 screws, 16mm
- 4 M3 screws, 30mm
- Pumps box
- Pumps lid
- Wire coat hanger

### Mounting the Parts to the Box

We're going to mount the pumps then install the plugs for the stirring motor and light on the front of the box. After that we will mount the circulating pumps on the sides of the box.

Pump unit box and parts

**Assembly:**

- Push the female barrel plug connectors into the smaller round holes on the front of the box. Secure them with the nuts that came with the connectors.
- Place each of the peristaltic pumps in large diamond shaped holes and screw each in with four 16mm M3 screws and nuts.
- Place the circulation pumps inside of the box, one on each side on the box. Use the manufacturer-provided mounting hardware and two 16mm M3 screws to secure each pump.

Pump box and parts

### Mounting and Wiring the Connectors

Next, we'll install the 8-pin and 12-pin connector sockets and wire them to the components in the box.

Phoenix connector parts

**Assembly:**

- Connect the 12-pin and 8-pin connector sockets with their mounting plates and use 2 M3 screws with each to attach them securely to the Pumps Box ccase.
- Cut and strip the wires on the pumps and barrel plug connectors.

### **Wire Order**

The connectors need to be wired the same as the ones in the Control Unit. The wiring order is further explained on the [MicroLab Wiring](/docs/wiring.md) page. It's important to maintain the same wiring order throughout the project.
<br>

### 8-pin wiring

The 8-pin connector is connected to the positive and negative power wires for the accessory port, the stir rod, the cooling unit pump and then heating unit pump.

- **Find the wires.** We describe the location of components as seen from the back on the box where you currently working.
- The top barrel connection is for the stir rod
- The bottom barrel connection is for the accessory port
- The left pump is for the Cooling Pump Unit
- The right pump is for the Heating Pump Unit

  Pump box and parts

- **Wire the 8-pin connector.** On the back on the 8-pin connector, from the left, insert and then screw down the power cables:

  - accessory positive (red)
  - accessory negative (black)
  - stir positive (red)
  - stir negative (black)
  - cooling pump positive (red)
  - cooling pump negative (black)
  - heating pump positive (red)
  - heating pump negative (black)

  Cable order

### 12-pin wiring

- **Wire the pumps.** Attach each of the connector ends of the stepper motor cables to one of the peristaltic pumps.
- **Wire the 12-pin connector.** Insert the stripped wire ends of the stepper motor cables into the back 12-pin connector socket. From left to right insert and then screw down the wires for the X and then Y and then Z cables.

  - Wire order. Each of the X, Y, and Z cables has 4 wires. From the left connect the wires in this order:
    - black
    - green
    - blue
    - red

  Cable order

<BR><BR>
Pump unit fully assembled with the lid open and wire connections visiblePump unit fully assembled with the lid open and wire connections visible

### Finishing it up

- NOTE: You may want to test everything before closing the lid.
- Use the four 30mm M3 screws to attach the lid to the box, closing it up.
- Place the coat hanger on top of the pumps Box and cut it so that it has approximately 3 inches of length beyond the pumps box on either side. Once it is cut, bend it so that it has two 90 degree bends at each end (see image below). Insert the ends into the holes in the top corners of the pumps box and use straps so that it can support the syringes when they are in use.

Wiring the pump wires

✨ 💖 ✨

Congratulations! You did it. Hopefully it wasn't too bad!

(Sorry if it was. We're trying to be encouraging here, not snarky.)

## Reactor Core Assembly

The Reactor Core houses the reaction chamber, which is where the SCIENCE happens. We're going to build the manifold, attach the stirring assembly, and put it all inside the mason jars!

 

### Parts

| Part ID   | Part Name                                     | Count | Notes  |
| --------- | --------------------------------------------- | ----- | ------ |
|           |                                               |
| RU-SRM    | Stir rod motor                                | 1     |
| RU-STR    | Stir rod                                      | 1     |
| RU-SRC    | Stir rod coupler                              | 1     |
| RU-COR    | Reactor manifold core (Printed)               | 1     | [Use this instead](https://github.com/FourThievesVinegar/microlab-parts/tree/master/additional-parts/reactor-manifold-GL45)
| RU-LID    | Reactor manifold lid (Printed)                | 1     | You don't need this part if you use the part linked above.
| RU-SRM    | Stir rod mount (Printed)                      | 1     |
| RU-RJF    | Jar Flanges (Printed)                         | 2     |
| RU-COR    | 250ml GL45 Borosilicate Glass Bottle          | 1     | 
| RU-OUT    | 32oz wide mouth mason jar for outer jacket    | 1     |
| RU-SDH    | Reactor stand - H (Printed)                   | 1     |
| RU-SDH    | Reactor stand - A (Printed)                   | 1     |
| RU-SDH    | Reactor stand - ¢ (Printed)                   | 1     |
| RU-SDH    | Reactor stand - K (Printed)                   | 1     |
| RU-TMP    | Thermistor                                    | 1     |
| RU-SYR    | Syringes                                      | 3     |
| CU-PLG    | Barrel plug connectors, 5.5mm x 2.1mm         | 2     | female |
| SP-M3S-12 | 12mm M3 screws with nuts                      | 3     |
| SP-M3S-20 | 20mm M3 screws with nuts                      | 3     |
| SP-STB    | Silicone tubing 8mm OD x 5mm ID               | 1     |

### Tools

- A hack saw or bolt cutter that can cut through the stirring paddle's shaft

#### Assembling the Reactor Core Manifold

v1.0 Reactor Core parts
Reactor stirring assembly assembled
Assembled reactor core

The printed manifold screws onto the GL45 250ml bottle, but first you have to carve the PTFE disc to fit between them and insert the stirrer through the central hole. Then you can use the shaft coupler to connect the motor to the stirrer. You may want to shim the motor with some tape to hold it more firmly in place. Then insert the whole thing into the main jar.

The trickiest thing is connecting the barrel plug connector to the motor. Soldering honestly helps here but you can also use thin solid-core wire (wires from ethernet cables are good for this) inserted into the motor's contacts.

#### Assembling and Attaching the Stirring Motor Mount

Next, we need to secure the stirring motor in place, and connect the motor shaft to the paddle.

**Parts:**

- Stir rod motor (RU-SRM)
- Stir rod (RU-STR)
- Stir rod coupler (RU-SRC)
- Stir rod mount - part of the manifold
- Possibly necessary: Material such as electrical tape to shim it in place.

**Assembly:**

- **Cut the PTFE disc.** It should be approximately 35mm across. The central hole for the stirrer shaft should be 8mm in diameter. The three holes around the edge should be 10mm in diameter but they don't need to be perfectly circular. 
- **Insert stir rod motor into manifold.** Place the stir motor into the recess at the top of the manifold. If it is loose, you may want to apply a small patch of electrical tape on the corners of the gearbox where there aren't any gears.
- **Attach stir rod motor to coupler.** Push the end of the stir rod coupler with the smaller hole over the motor's shaft and secure it with one of the set screws that came with the coupler.
  - Take care to center it and be aware that the shaft likely has a flat spot that makes it non-symmetrical
- **Wire the motor.**
  - This is one place where soldering may come in handy. The motor in the parts list does not have built-in leads. It is possible to add leads using small solid-core wires, such as those from an ethernet cable. You can strip extra length, feed the wires through the contacts on the motor, then use pliers to fold and twist the wires to themselves to maintain contact. In this case, wrapping with electrical tape, hot glue, or heat shrink is advised. You can use a 2x lever connector to attach the motor leads to the barrel plug connector.
- **Insert stir rod through the disc into the coupler.** Strip a few mm of PTFE coating from the end of the stirrer's shaft. Then thread it through the central hole in the PTFE disc and insert it through the central hole in the manifold up into the shaft coupler attached to the motor
- **Connect stir rod to coupler.** Tighten the set screws on the coupler to connect the stirrer to the motor.
- **Be ready to resize.** When fully assembled, the mixing paddle should be suspended in the reaction chamber and should not touch the bottom or sides of the chamber. You will likely need to cut the stirrer's shaft short for this to fit properly. Take your time when cutting the shaft, as cutting it too short will make it impossible to use.

  Reactor manifold assembled

### Reactor Unit reaction chamber assembly

Almost there! Now we just have to put it all together!

**Parts:**

- 250ml Bottle
- 32oz Mason jar and lid ring

**Assembly:**

- Lower the stir rod into the bottle, screwing the bottle into the manifold.
  - If the stir rod shaft is too long, you will need to remove the it from the manifold, cut it shorter using a hacksaw or bolt cutters, and then reattach it.
- Place the bottle inside the larger 32oz jar, slide the 32oz jar lid ring over top the manifold and screw it onto the jar.

TADA! Your Reactor Core is complete!

Assembled reactor core

### Reactor Unit Assembly

These instructions assume you have already assembled the Pumps Box and the Reactor Core.

Reactor unit fully assembled

### Assembling the Stand

**Parts:**

- 250ml GL45 Borosilicate Glass Bottle (RU-COR)
- 32oz wide mouth mason jar for outer jacket (RU-OUT)
- Reactor stand - H (Printed) (RU-SDH)
- Reactor stand - A (Printed) (RU-SDA)
- Reactor stand - ¢ (Printed) (RU-SDC)
- Reactor stand - K (Printed) (RU-SDK)

Reactor stand parts

Reactor stand assembled

**Assembly:**
Reactor unit fully assembled

Reactor unit fully assembled

- Assemble the Reactor Stand:
  - **Connect H and A**

    - Place the H on the left, tilted up in its left side, the top "arms" of the H at the back should have 2 slots.
    - Place the A at the back tilted on its left side so the "feet" of the A line up with the top of the H.
      Reactor stand assembled
      Reactor stand assembled
    - Slide the hooks on the A into the slots on H

  - **Connect the A and K**

    - A is already positioned
    - Place the K on the right, tilt it up on its left side so A can hook into the two slots on the K.

      Reactor stand assembled

  - **Connect the ¢ to the H and K**

    - Position the ¢ between the H and K with the empty space of the C opening at the front. The ¢ is attached at the top, the two hooks on either end of the ¢ will line up with the 2 slots on the H and an on the K.

        Reactor stand assembled

  Reactor stand assembled

### Reactor Unit - Putting it All Together

You've already built the core and the pump. All that's left to do is connect it all up.

**Parts:**

- Reactor Stand
- Reactor Core
- Pumps Unit
- Jar Flanges (Printed) (RU-RJF)

**Assembly:**

- **Attach the Pumps box to the Reactor Stand.**
  - Take the Pumps Box and insert the tabs on H, ¢ , and K

Reactor stand assembled

- **Attach the Reactor Core**

  - Place the Reactor Core in the center of the ¢.
  - Add the jar flanges (C shaped pieces) as shims in between the top of the ¢ part and the Reactor Core's outer jar. Two flanges should keep it snugly in place. If not, consider using another shim. (See picture below for reference, the jar flanges are orange and the ¢ piece is yellow.)

- **Connecting Reactor Core to Pumps Box**
  - Plug the stirring motor's plug into the upper barrel connector socket on the Pumps Box.
  - Attach one piece of tubing to each of the the peristaltic pumps and through the holes in the Reactor Core manifold to reach the 6oz mason jar chamber.

Reactor stand assembled 

This concludes the assembly instructions for the Reactor Unit. Next up: [MicroLab Setup & Operation](/docs/operation.md).

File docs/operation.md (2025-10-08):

# Setting Up and Operating the MicroLab

## Setting it up

This section describes how to assemble a complete but disassembled MicroLab. If you need to build one from scratch, see the links in the next section.

## Parts

* [Reactor Unit](/docs/assembly-reactor-unit.md)
* [Heating Unit](/docs/assembly-temperature-exchangers-unit.md)
* [Cooling Unit](/docs/assembly-temperature-exchangers-unit.md)
* [Control Unit](/docs/assembly-control-unit.md)
* [MicroLab Cables](/docs/assembly-control-unit.md#cables)
* Cable - USB cord on Thermistor (RU-TMP)
* [MicroLab Tubing](/docs/assembly-temperature-exchangers-unit.md#tubing) (6 pieces, four 16" and two 8")
* Power - MicroLab power supply (CU-POW)
* Power - Switchable power strip or aquarium temperature controller (unless using a self-regulating heat source like a deep fryer)
* Cable - Power cord on submersible heater (TC-SBH) (unless using a self-regulating heat source like a deep fryer)
* Propylene glycol or other liquids (TC-LIQ) for the heating unit, cooling unit, and reactor core

Reactor stand assembled

## MicroLab Assembly

* [Setting up the Reactor Unit](#reactor)
* [Setting up Heating Unit](#heat)
* [Setting up Cooling Unit](#cool)
* [Cabling the Control Unit](#control)

## Setting up the Reactor Unit

- **Assembled Reactor Unit.** If not already assembled, put together the stand, add the Pumps Box and Reactor Core. You can refer to [Building the Reactor Unit](/docs/assembly-reactor-unit.md) for more information.
- **Add outer chamber liquid.** Unscrew the 32 oz mason jar outer chamber lid ring. Lift up the manifold lid and add the liquid to the jar. Re-seat the manifold and screw the lid ring back to secure the manifold. You may need to add more liquid after running the circulation pumps.
- **Add Thermistor** Insert Thermistor in the slightly larger opening on the manifold so the probe reaches the temperature control liquid.

  Reactor stand assembled

## Setting up the Heating Unit

- **Add fluid.** Take the Heating Unit, unscrew the ring and lift up the heating lid. Add the liquid, return the lid and screw the lid ring back on.
- **Add tubing**. The 3 pieces of tubing connect heating unit, pump and reactor core.
  * Attach one 16" piece of silicone tubing from the top of heating circulation pump to Reactor Core manifold. Be sure the tubing goes through the manifold and down a couple inches below the liquid's surface.
  * Attach one piece of 8" silicone tubing from the bottom of heating circulation pump to one of the copper tubes on the Heating Unit.
  * Attach one 16" piece of silicone tubing from Heating Unit copper tube to the Reactor Core manifold.
- **Heat the liquid** When you are ready to run the recipe, plug the submersible heater into the switched power strip or aquarium temperature controller and allow it to run and heat up the water.

Temp Tubing

## Setting up the Cooling Unit

- **Add cold fluid.** Take the Cooling Unit, unscrew the ring and lift up the cooling lid. Add the liquid and ice, return the lid and screw the lid ring back on.
   * You may need to experiment with water, ice and additives to get the best cold temperature that lasts as long as you need.
   * You may want to use a bigger container than a mason jar for the ice bath. A cooler full of ice will also work. Make sure that your circulating fluid does not freeze in whatever you use.
- **Add tubing**. The 3 pieces of tubing connect cooling unit, pump and reactor core.
  *  Attach one 16" piece of silicone tubing from the top of cooling circulation pump to Reactor Core manifold. Be sure the tubing goes through the manifold and down a couple inches below the liquid's surface.
  * Attach one piece of 8" silicone tubing from the bottom of cooling circulation pump to one of the copper tubes on the Cooling Unit.
  * Attach one 16" piece of silicone tubing from Cooling Unit copper tube to the Reactor Core manifold.

Temp Tubing

## Cabling the Control Unit

The Control Unit will need to be connected to the power supply, the Pumps box (to run the pumps and power the ports), and the Thermistor.

Temp Tubing

* **8-pin cable** connects the 8-pin cable to mounted 8-pin connector on the Control Unit box and on the Pumps Box.
* **12-pin cable** connects the 12-pin cable to mounted 12-pin connector on the Control Unit box and on the Pumps Box.
* **Connect Thermistor USB to Control Unit** Plug the USB end of the Thermistor into the Control Unit's USB port.
* **Plug in Power supply** Insert the barrel connector of the power supply to the barrel connector power port on the Control Unit.

Temp Tubing

The MicroLab should now be connected and ready to be setup up for a recipe and run.
* The picture below shows the syringes attached, we left that step for later when actually using it, but wanted to show the connected MicroLab in all its glory.

Temp Tubing

## Getting Started Using Your MicroLab

When you add power to the Control Unit, it will turn on. You should a see start-up sequence on the touchscreen.

Once your MicroLab is set up it just needs a recipe to run, the ingredients loaded, and some human actions during the recipe making.

## MicroLab Recipes

Recipes are a set of instructions the MicroLab uses to run chemical reactions. They are created on the Recipe Press site.

### About Recipes

Temp Tubing

A recipe is a series of numbered steps. Each step has:
 * User message - test displayed on the touchscreen
 * Task type - action the MicroLab will take
 * Task icon - icon that will display on touchscreen
 * User Option(s) - "links" to next steps that depend on user input or judgement (used with Human Tasks)
 * Detailed description - more text that can be shown on the touchscreen

   Recipe Press Logo

The MicroLab is able to perform 5 task types:
* Human Task - pause until the person completes the task shown on the touchscreen and taps on a menu button to move to the next stop
* Pump - turn one pump on to dispense a set volume of liquid over a certain period of time (while optionally stirring and maintaining a temperature)
* Stir - activate the stir rod for a set period of time with optional task to maintain temperature
* Cool - cools the reactor jacketing liquid to the set temperature
* Heat - heats the reactor jacketing liquid to the set temperature

### The Test Recipe

We have a Test Recipe designed to check that all the parts of the MicroLab are working correctly. It is available on the Recipe Press site and is also preloaded on the Control Unit.

On the Press Recipe site, you can see the how the Test Recipe is built.

Recipe Press Logo

#### **Closer Look at Step 0**

Let's take a look at Step 0 to see how a step works. Step 0 is where the MicroLab greets the human and asks if they want to continue.

**Step details:**
* User message is the greeting
   * "Hello and welcome! This recipe is to test the function of the microlab. Ready to see the test options?"
* Task type is Human Task, the Microlab is waiting for a User Option or Menu button to be selected.
* Task icon - shows the Human Task icon
* User Option(s) - there is one option, called "Yes", it sets the next step to Step 1.
* Detailed description - this field is empty in step 0
Recipe Press Logo

The Recipe Press also allows you to simulate your recipe:

Recipe Press Logo

#### Test Recipe Steps

When running the recipe you are able to test the X pump, Y pump, Z pump, stir rod, and temperature control.

The MicroLab is able to do these tests by using and reusing its 10 steps.

* Step 0: Human Task - Welcome
* Step 1: Human Task - Select test for pumps, heating or stirring
* Step 2: Pump - Test Pump X
* Step 3: Pump - Test Pump Y
* Step 4: Pump - Test Pump Z
* Step 5: Human Task - Ask if they want another test
* Step 6: Heat - Heat to 30C
* Step 7: Human task - Shows action complete, ask if they want another test
* Step 8: Stir - use stir rod for 10 seconds
* Step 9: Human task - Shows action complete, ask if they want another test
* Step 10: Human task - Confirmation that user tapped no to doing another test and test is complete

## Using a Recipe

Before starting a recipe:
* Set up the MicroLab
* Have Heating Unit reach the needed temperature
* Have Cooling Unit reach the needed temperature
* Load the syringes with the needed liquid ingredients
* Load the inner reaction chamber with needed ingredients

With the Test Recipe you:
* Set up the MicroLab
* Load the syringes with water and attach to the top three peristaltic pumps
* Let the Heating Unit heat up
* Setup the Cooling Unit

Once ready, use the touchscreen to start the Test Recipe. follow the steps to test each pump and confirm the contents of syringes enter the chamber. Run the heating and confirm the MicroLab heats the chamber to 30C. Run the stirring and confirm the stir rids runs for the appropriate time. Once all tests are complete, you can exit the recipe.  

## Writing a Recipe

New recipes can be made online, downloaded to a thumbdrive and then uploaded to the Control Unit.  

You make a recipe directly on the [Recipe Press site](https://recipe-press.fourthievesvinegar.org/).

Another option is to start [a project in Vinni](https://vinni.fourthievesvinegar.org/projects/NVXg2yPAKaMu) and save your recipes that way.
   * More on this as Vinni approaches a real release and our services get integrated.

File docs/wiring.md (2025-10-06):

# MicroLab Wiring Guide

The most important part of wiring is to be consistent throughout the project.

We use two kinds of wires for connecting the electronic components in the MicroLab:
* 16 gauge wire in blue, red, green, black (ethernet cables and their wires will also work)
* 22 gauge breadboard jumper wire

Several of the boards and connectors have a fairly straight forwarding wiring. For example the barrel connectors have 2 wires for power, one red (positive) and one black (negative).

* Relay Board
* 12v to 5v converter
* Arduino
* Raspberry Pi

There are two connectors that have more complex wiring: the 8-pin and 12-pin mountable screw terminal connectors.

This style of connector has 3 pieces: socket, mount plate and plug.

Panel-mounted components installed

<BR><BR>

###  **8-pin Wire Order:**

Note: It's important to maintain the same wiring order throughout the project.

The 8-pin connector passes 12V along to the Accessory port (Acc), Stir rod (Stir), Cooling pump (Cool), and Heating pump (Heat) wires.

There are four 8-pin connectors that will need to be wired. One mounted to the Control Unit and one mounted to the Pumps Box. The other two are for the ends of the 8-pin MicroLab cable used to connect the 8-pin connectors on both boxes.

**Front order - 8-pin connector - external & cable**
If looking at the front of 8-pin socket connector from outside the case, from left to right the wires will go:
* Heat negative (-), black
* Heat positive (+), blue
* Cool negative (-), black
* Cool positive (+), red
* Stir negative (-), black
* Stir positive (+), green
* Accessory negative (-), black
* Accessory positive (+), black

This is the same order for placing the wires at the back of the 8-pin socket for MicroLab cable.

Panel-mounted components installed
<BR><BR>

Cable order
<BR><BR>

**Reverse order - 8-pin connector - internal**
From inside the case, looking at the back of the 8pin connector then the wiring order will be reversed and look like this:

Cable order

###  **12-pin Wire Order:**
Note: It's important to maintain the same wiring order throughout the project.

The 12-pin connector passes 12V along to three peristaltic pumps. When viewed from front of pumps box they are named X, Y, and Z.

Cable order

The stepper motor cable that comes with the pumps will be cut in half and the cut ends stripped (you will likely need much less than half), creating 6 cables. Three will be used in the Control unit and three will be used in the Pumps Box.

There are four 12-pin connectors that will need to be wired. One mounted to the Control Unit and one mounted to the Pumps Box. The other two are for the ends of the 12-pin cable used to connect the 12-pin connectors on both boxes.

### **12-pin connector - internal**.
The 12-pin connector passes 12V to the three peristaltic pumps. From inside the case, we'll wire the back of the 12-pin connector. When attaching the stripped wires to the back of the 12-pin connector socket the order is from left to right:
  * Pump Z cable - black wire
  * Pump Z cable - green wire
  * Pump Z cable - red wire
  * Pump Z cable - blue wire
  * Pump Y cable - black wire
  * Pump Y cable - green wire
  * Pump Y cable - red wire
  * Pump Y cable - blue wire
  * Pump X cable - black wire
  * Pump X cable - green wire
  * Pump X cable - red wire
  * Pump X cable - blue wire

NOTE: Your cables may differ from these - the color and order can vary between different manufacturers. When in doubt, keep the order consistent with the cables that shipped with your pumps / motors.

  Cable order

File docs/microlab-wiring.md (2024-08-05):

# MicroLab Wiring Guide

The most important part of wiring is to be consistent throughout the project.

We use two kinds of wires for connecting the electronic components in the MicroLab:
* 16 gauge wire in blue, red, green, black
* 22 gauge breadboard jumper wire

Several of the boards and connectors have a fairly straight forwarding wiring. For example the barrel connectors have 2 wires for power, one red (positive) and one black (negative).

* Relay Board
* 12v to 5v converter
* Arduino
* Raspberry Pi

There are two connectors that have more complex wiring: the 8-pin and 12-pin mountable screw terminal connectors.

This style of connector has 3 pieces: socket, mount plate and plug.

Panel-mounted components installed

<BR><BR>

###  **8-pin Wire Order:**

Note: It's important to maintain the same wiring order throughout the project.

The 8-pin connector passes 12V along to the Accessory port (Acc), Stir rod (Stir), Cooling pump (Cool), and Heating pump (Heat) wires.

There are four 8-pin connectors that will need to be wired. One mounted to the Control Unit and one mounted to the Pumps Box. The other two are for the ends of the 8-pin MicroLab cable used to connect the 8-pin connectors on both boxes.

**Front order - 8-pin connector - external & cable**
If looking at the front of 8-pin socket connector from outside the case, from left to right the wires will go:
* Heat negative (-), black
* Heat positive (+), blue
* Cool negative (-), black
* Cool positive (+), red
* Stir negative (-), black
* Stir positive (+), green
* Accessory negative (-), black
* Accessory positive (+), black

This is the same order for placing the wires at the back of the 8-pin socket for MicroLab cable.

Panel-mounted components installed
<BR><BR>

Cable order
<BR><BR>

**Reverse order - 8-pin connector - internal**
From inside the case, looking at the back of the 8pin connector then the wiring order will be reversed and look like this:

Cable order

###  **12-pin Wire Order:**
Note: It's important to maintain the same wiring order throughout the project.

The 12-pin connector passes 12V along to three peristaltic pumps. When viewed from front of pumps box they are named X, Y, and Z.

Cable order

The stepper motor cable that comes with the pumps will be cut in half and the cut ends stripped, creating 6 cables. Three will be used in the Control unit and three will be used in the Pumps Box.

There are four 12-pin connectors that will need to be wired. One mounted to the Control Unit and one mounted to the Pumps Box. The other two are for the ends of the 12-pin MicroLab cable used to connect the 12-pin connectors on both boxes.

### **12-pin connector - internal**.
The 12-pin connector passes 12V to the three peristaltic pumps. From inside the case, we'll wire the back of the 12-pin connector. When attaching the stripped wires to the back of the 12-pin connector socket the order is from left to right:
  * Pump Z cable - black wire
  * Pump Z cable - green wire
  * Pump Z cable - red wire
  * Pump Z cable - blue wire
  * Pump Y cable - black wire
  * Pump Y cable - green wire
  * Pump Y cable - red wire
  * Pump Y cable - blue wire
  * Pump X cable - black wire
  * Pump X cable - green wire
  * Pump X cable - red wire
  * Pump X cable - blue wire

NOTE: Your cables may differ from these - the color and order can vary between different manufacturers. When in doubt, keep the order consistent with the cables that shipped with your pumps / motors.

  Cable order

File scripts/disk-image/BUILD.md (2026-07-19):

### Building the Image on macOS via Docker

> These steps assume you have Docker toolchain installed on your Mac and that you have already cloned the repository into `microlab-image/`.

1. **Build the "builder" image**  
   From the project root (where `Dockerfile.builder` lives), run:
   ```bash
   docker build -f Dockerfile.builder -t microlab-image-builder .
   ```

2. **Register ARM translator**
   ```bash
   docker run --rm --privileged tonistiigi/binfmt --install all
   ```

3. **Run the build inside Docker**
   This will mount your workspace into the container, create loop devices, mount partitions, and invoke the standard build script. The `--privileged` flag is required so the container can manage loopback devices and mounts.

   ```bash
   # This will build the latest from the main branch
   docker run --rm --privileged -v "$(pwd)":/workspace microlab-image-builder \
        bash -lc "cd /workspace && bash scripts/build-image.sh"   
   ```
   
   To target a particular release tag, add it after the `build-image.sh` script

   ```bash
   # This will build from the v1.0.1 tag
   docker run --rm --privileged -v "$(pwd)":/workspace microlab-image-builder \
        bash -lc "cd /workspace && bash scripts/build-image.sh v1.0.1"   
   ```

4. **Retrieve your image**
   When the container finishes, you’ll find:

   ```
   microlab-image/build/raspios-microlab.img
   ```

   ready to flash to an SD card.

5. **(OPTIONAL) Troubleshoot the `microlab-image-builder` Docker Image**
   ```shell
   docker run --rm -it \ 
     --privileged \   
     -v "$(pwd)/build:/build:ro" \   
     --entrypoint /bin/bash \   
     microlab-image-builder
   ```

6. **(OPTIONAL) Inspect your image**
   ```bash
   docker run --rm -it \
     --privileged \
     -v "$(pwd)/build:/build:ro" \
     microlab-image-builder \
     /workspace/scripts/inspect-raspios-microlab.sh /build/raspios-microlab.img
   ```

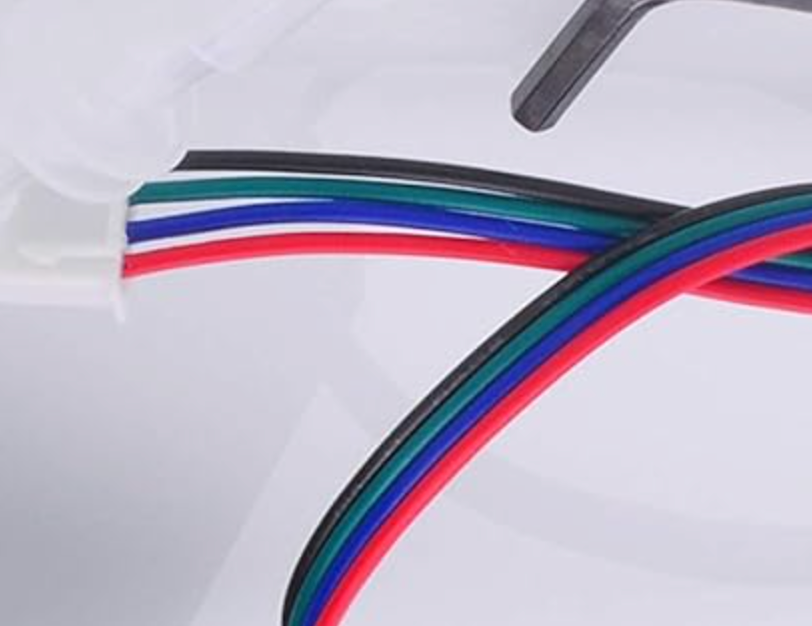
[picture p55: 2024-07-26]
docs/media/control-unit/step_cable.png

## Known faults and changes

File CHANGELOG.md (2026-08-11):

# Changelog

## [Unreleased]

### Added

### Changed

## [1.0.4]

### Changed
- Updated thermometer reading to better handle errors and reset connection when errors persist

## [1.0.3]

### Changed
- Tweaked control box lid tolerances
- Updated build scripts to include Matchbox window manager to fix file upload dialog usability issues

## [1.0.2]

### Changed
- Fixed unreliable Chromium browser installation

## [1.0.1]

### Added

- Build scripts for disk image merged into main repo
- Custom GRBL included in main repo
- Parts files included in main repo

### Changed

- Updated docs generally and to reflect included scripts

## [1.0.0]

### Added

- Support for controlling gpio pins on the arduino when using custom grbl firmware. (#282)
- Ability to delete recipes from the microlab on the recipe details page. (#288)
- New `microlab-image` [build scripts](https://github.com/FourThievesVinegar/microlab-image)

### Changed

- New display support and GUI updates
- Updated docs with new reactor core
- Added alphabetical navigation of the recipe list. (#273)
- Extra validation for hardware config files. Hardware components are now automatically sorted by dependencies to prevent them from loading out of order. (#269)
- Syringe pump and peristaltic pump implementations no longer directly open a serial connection to grbl, and config instead now references a grbl device. (#282)
- Upgraded `gpiod` library and corresponding `gpiod_chip` client to v2.3.0 (#298)
- Refactored code for Pythonic compliance: added type hints, enhanced readability, and fixed minor type-checking bugs. 
- Performance improvements, such as caching for `localization.load_translation` function or replacing `time.sleep` with synchronization primitives.
- Improved multiprocess queues lifecycle management.
- Expanded UnitTests
- Expanded usage of Pydantic models

## [0.6.0]

### Added

- Slowly dispense reagents over time.
- Many pre-release tweaks and bug fixes.
- Massive docs update.
- New printable cases, stands, and reactor parts.
- Ability to manually reload hardware from the settings menu. (#197)
- Hardware settings are configurable from the UI in a basic fashion (#141).
- v0.6 hardware config supports PID temperature control
- MicroLab 0.5 simulation configuration (#140).
- Configurable hardware limits for supported temperatures. Recipes that require values outside of the configured range will no longer run. (#146).
- Sounds that play on recipe completion, errors, and user input steps (#149).
- Page for viewing logs on the frontend (#158).
- Uses the 4TV color palette (#157)
- Dark mode! (#81)

### Changed

- Performance and logging tuning
- Configuration is now stored in /etc/microlab instead of backend/config.py (#141).
- Recipe data was moved from /backend/recipes/files to being stored by default at /var/lib/microlab/recipes. Recipes in the repository are kept at backend/data/recipes and copied to their proper storage location at launch. (#141).
- Hardware configuration files were moved from backend/hardware to being stored by default at /var/lib/microlab/controllerhardware and /var/lib/microlab/labhardware. Hardware configurations in the repository are kept at backend/data/hardware and copied to their proper storage location at launch. (#141).
- The API endpoints `/start/<name>`, `/stop`, `/select/option/<name>`, `/controllerHardware/<name>`, `/labHardware/<name>` are now POST rather than GET. (#144).
- Hardware upgrades including but not limited to #74 and #83

### Fixed

- Bug when multiple gpiod instances were being used (#141).
- Syringe pump configuration was not being used (#118).
- Error responses no longer return status code 200. (#144).
- Kiosk mode now properly launches and restore dialog not shown (#133)
- Uploading recipes now immediately shows the uploaded recipe in the recipe list (#236)

### Removed

- Celery and redis (#139).

## [0.5.1]

## [0.5.0]

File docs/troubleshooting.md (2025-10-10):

# MicroLab Troubleshooting

## A Note about where to start

The MicroLab is essentially a Linux box with an Arduino and some relays attached. You can always connect a keyboard to the open USB slot, hit ctrl + alt + F6 and log in as `thief` pw: `vinegard`. From here, if you know your way around a POSIX/Linux/Unix terminal, you can poke around. Check out [os-services.txt](https://github.com/FourThievesVinegar/solderless-microlab/blob/main/docs/os-services.txt) for more about how the MicroLab interfaces with the operating system.

If you haven't ever seen a linux terminal before, BE NOT AFRAID! It's the same files / directories as any other computer but instead of double-clicking the folder, you type `cd my-folder`. To list what's in the folder, you type `ls`. To edit a text file, you type `nano my-cool-file`. You can [learn more here](https://ubuntu.com/tutorials/command-line-for-beginners#1-overview).

## I'm getting an error when I start the MicroLab

Open the menu and go to the Status page. You should see a button that says 'Reload Hardware'. Tap it gently until the status changes to "idle".

## My stepper motors are being weird! Stepper Motor Calibration

We will need:

- Raspberry Pi that is set up
- Arduino that is set up
- Peristaltic pumps with stepper motors
- Small phillips head screw driver

### Potentiometer tuning

- On the Arduino, each A4988 stepper motor driver board has a small potentiometer that looks like a small phillips head screw on the board.
- If your peristaltic pumps are acting strange (not turning, or moving erratically), you **DEFINITELY** want to tune the potentiometers. In a worst-case scenario, motors may be damaged by excess voltage.

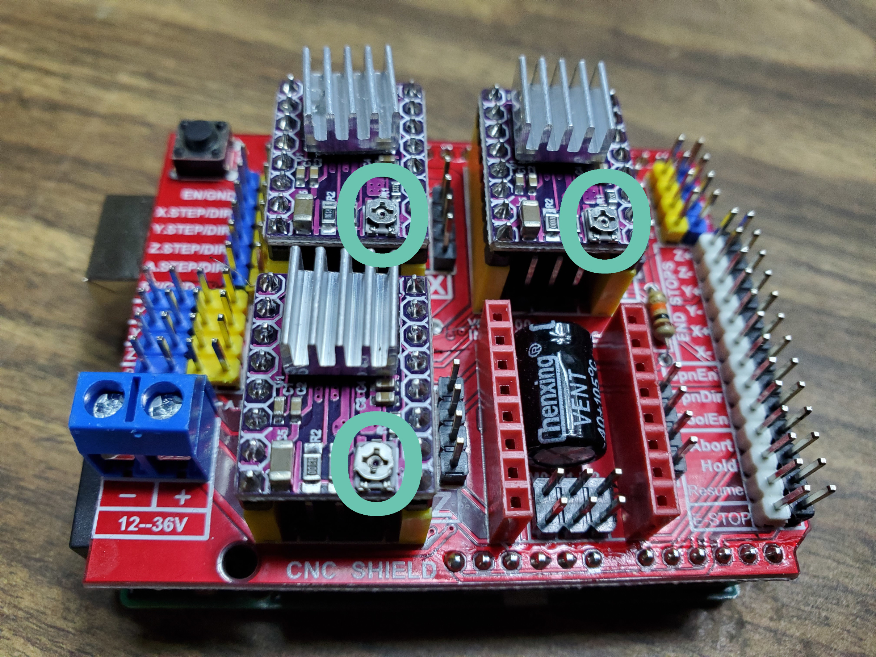
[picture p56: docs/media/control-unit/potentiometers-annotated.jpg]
Potentiometer


Note:
In the image above, the potentiometers are circled and their slightly-flat sides are pointed to the left. This is the "slightly-open" position.

**WARNING!** Failure to correctly tune the potentiometers can damage the motor controller and the motors themselves.

#### How to tune

You will **gently** turn the potentiometers on the motor control boards clockwise or counter-clockwise using a small phillips head screw driver. Be careful to stop once there is any resistance, do not to turn past the resistance.

- Turning them clockwise "closes" the voltage down
- Turning them counter-clockwise "opens" the voltage up

1. Attach the Arduino's stepper motor cables to the stepper motor on the peristaltic pump.
1. Double-check that everything is connected properly.
1. Start with the potentiometers in the "closed" position.
1. Connect the Arduino to the Pi.
1. Power on the Raspberry Pi, the Arduino shield and the pumps.
1. On the Raspberry Pi, the MicroLab software will load. Load the Test Recipe and choose the Reagent Pumps test. This test will allow you to make the pumps each dispense 10ml.
1. When the potentiometer is "closed" nothing should happen. Slowly turn the potentiometer counter-clockwise an eighth of a turn at a time to "open" them. Check if the stepper motors turn smoothly. If they do not move, "open" the potentiometer an eighth-turn and try again. If they move erratically, your voltage is likely too high and you need to "close" the potentiometer.

- You can tune the potentiometers at any time, but it is easiest during assembly when the Control Unit case is open.

### Stepper motor verification

**This is a more in-depth way to test the function of the stepper motors. If you have tuned the potentiometers as described above and the motors turn smoothly, you do not need to perform these steps.**

Check each peristaltic pump's motor. With the cables and power disconnected, you should be able to spin the shaft of the stepper motor with your fingers and feel almost no resistance.

Testing the motor. Take a short length of wire and jumper the top two pins (Pins 1 and 2) of the connector together.

If the motor is wired correctly you should now feel some resistance when you spin the shaft (you should be able to feel the “steps” in the stepper motor). Repeat this procedure with the bottom two pins (Pins 3 and 4).

If you do not feel any change in resistance, try jumpering other combinations of pins until you identify the two pairs. See Troubleshooting Stepper Motor if you continue to have issues.

## My circulation pumps don't have mounting brackets! - Pumps Box Assembly

- If your pump does not come with mounting hardware, you may need to get creative. In a pinch, zipties should work. You may want to double them up or drill out the holes to support thicker ties.

## My Reactor Core is failing somehow!

Make sure you are using the new GL-45 reactor core. The previous multi-part manifold was not chemically or thermally resistant.

## My Stirrer is Wobbly!

You can adjust the alignment of your stirring rod by loosening the top set screws on the shaft coupler, carefully religning the coupler with the motor, and tightening the set screws again. Make sure the central hole in the PTFE disc is centered.

## Optimizing Heat Exchange

We recommend having a heat reservoir and a cold reservoir. This can be as simple as a small counter-top deep fryer with operational temperatures below 188.2 °C / 370.8 °F (the boiling point of propylene glycol) and a cooler of ice (or a small chest freezer). We're currently testing these and if you've got ideas, please [reach out](https://fourthievesvinegar.org/contact/)!

## My touch screen is messed up! - Touch Screen Settings

### The screen doesn't work

The small touchscreen doesn't work at all. It shows all white or fails to light up at all.

**Issue:**
Touchscreen doesn't light up at all

**Solution:**
This indicates a hardware problem. It's likely the screen isn't getting power or is broken. If you have extra screens or microcomputers, try a different screen or another computer. If none of this resolves the issue, you may need to order a replacement or reach out to the manufacturer for help

### X or Y touch screen axis is reversed

**Issue:**
Your touch screen works, but not correctly. Tapping near two of the corners kinda works, but the other two corners seem reversed.

**Solution:**
There is a configuration file change that should fix this. Open the following file.

```bash
sudo nano /etc/X11/xorg.conf.d/99-calibration.conf
```

Look for a line like this one:

```bash
Option "SwapAxes" "1"
```

Try changing that `"1"` to a `"0"` and restarting the Pi.

```bash
sudo shutdown -r now
```

If that doesn't work, try searching for the manufacturer and model number of your screen with terms like "swapped axes".

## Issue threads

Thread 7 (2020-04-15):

FourThievesVinegar/solderless-microlab #7: Additional Instructions?

samhavens, 2020-04-15:
Some additional instructions that may be helpful... Might be worth adding

* [Emulating a Raspberry Pi with Virtualbox](https://raspberrytips.com/run-raspberry-in-virtual-machine/)
* Hardware shopping list
  * rasberry pi 3 - (link)
  * [DC, stepper motor control + limit switch](https://www.aliexpress.com/item/Free-shipping-cnc-shield-v3-engraving-machine-3D-Printer-4pcs-A4988-driver-expansion-board-for-Arduino/32808916949.html)
  * [Interface + buttons](https://www.aliexpress.com/item/Free-shipping-LCD-module-Pi-TFT-3-5-inch-320-480-Touchscreen-Display-Module-TFT-for/32587995145.html)
  * [Relay board](https://www.aliexpress.com/item/1PCS-Raspberry-Pi-Power-Relay-Board-Expansion-Module-Shield-Supports-RPi-A-B-2-B-3/32961638909.html)
  * [Temperature](https://aliexpress.com/item/32827261401.html)
  * [some stepper motors with female headers](https://www.aliexpress.com/item/32853499120.html)

samhavens, 2020-04-15:
Hmm, it doesn't seem like emulating the Pi works, `RPi.GPIO` still seems to be aware it isn't actually running on a Pi.

I will dig out my Pi knockoff and see if that works. Otherwise, I will wait for the Pi I ordered to arrive

SpikeNebula, 2020-04-18:
Theo added the parts list in eccdbb76175f4592914c61e4e946cad9d0eba75c

myrinzic, 2023-01-17:
Leantime ticket #112

sparklestheunicorn, 2023-10-04:
This should be all set

closed 2023-10-04 by sparklestheunicorn

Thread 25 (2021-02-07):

FourThievesVinegar/solderless-microlab #25: Finish hardware readme

mis4mike, 2021-02-07:
There is currently a partial README.md file in the hardware directory of the project. This needs to be updated with:
- A complete list of parts (specs, manufacturer numbers, where to get them etc.). This includes types of syringes, tubes, printing recommendations, and all electronics. Preferably with pics.
- A complete list of assembly steps with pics.
- If anyone has a completed prototype and can provide any specs, that would be awesome!

myrinzic, 2023-01-17:
Leantime ticket #111

myrinzic, 2023-01-17:
Leantime Ticket 111

sparklestheunicorn, 2023-10-04:
This is largely complete (more details and pics are required in docs/operation.md). Separate issues can be made for updating particular parts of the documentation.

closed 2023-10-04 by sparklestheunicorn

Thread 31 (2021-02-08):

FourThievesVinegar/solderless-microlab #31: 500 Error from backend when accessing /select/option/Done

mis4mike, 2021-02-08:
I get this error when I proceed on a development machine through the aspirin recipe. It seems to happen after the final manual step.
```
GET http://localhost:5000/select/option/Done 500 (INTERNAL SERVER ERROR)
```
The error on the python client is:
```
[2021-02-07 19:29:33,159] ERROR in app: Exception on /select/option/Done [GET]
Traceback (most recent call last):
  File "/home/mike/workspace/solderless-microlab/backend/env/lib/python3.6/site-packages/redis/connection.py", line 552, in connect
    sock = self._connect()
  File "/home/mike/workspace/solderless-microlab/backend/env/lib/python3.6/site-packages/redis/connection.py", line 609, in _connect
    raise err
  File "/home/mike/workspace/solderless-microlab/backend/env/lib/python3.6/site-packages/redis/connection.py", line 597, in _connect
    sock.connect(socket_address)
ConnectionRefusedError: [Errno 111] Connection refused

During handling of the above exception, another exception occurred:

Traceback (most recent call last):
  File "/home/mike/workspace/solderless-microlab/backend/env/lib/python3.6/site-packages/celery/backends/redis.py", line 127, in reconnect_on_error
    yield
  File "/home/mike/workspace/solderless-microlab/backend/env/lib/python3.6/site-packages/celery/backends/redis.py", line 177, in _consume_from
    self._pubsub.subscribe(key)
  File "/home/mike/workspace/solderless-microlab/backend/env/lib/python3.6/site-packages/redis/client.py", line 3528, in subscribe
    ret_val = self.execute_command('SUBSCRIBE', *iterkeys(new_channels))
  File "/home/mike/workspace/solderless-microlab/backend/env/lib/python3.6/site-packages/redis/client.py", line 3416, in execute_command
    self.shard_hint
  File "/home/mike/workspace/solderless-microlab/backend/env/lib/python3.6/site-packages/redis/connection.py", line 1185, in get_connection
    connection.connect()
  File "/home/mike/workspace/solderless-microlab/backend/env/lib/python3.6/site-packages/redis/connection.py", line 557, in connect
    raise ConnectionError(self._error_message(e))
redis.exceptions.ConnectionError: Error 111 connecting to localhost:6379. Connection refused.

During handling of the above exception, another exception occurred:
```

thenixlabs, 2021-02-22:
Looks like you don't have the redis server running. On the pi you would need install the following packages:

sudo apt -y install screen git redis-server python-celery-common python3-flask python3-pip  python3-rpi.gpio python3-serial

"redis-server" is what you are missing. If you are running on a platform not based on debian take a look at https://redis.io/

mis4mike, 2021-02-28:
Thanks! Adding this to the setup documentation.

closed 2021-02-28 by mis4mike

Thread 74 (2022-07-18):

FourThievesVinegar/solderless-microlab #74: Manifold needs a hole for the temperature probe.

mis4mike, 2022-07-18:
Currently there's no dedicated hole in the manifold for the temperature probe. Its already tight jamming the temp control tube into the manifold top, so we could use a dedicated place for it.

myrinzic, 2023-01-17:
Leantime Ticket 92

sparklestheunicorn, 2023-11-13:
> > Currently there's no dedicated hole in the manifold for the temperature probe. Its already tight jamming the temp control tube into the manifold top, so we could use a dedicated place for it.
> 
> create a special repository and store it there

We do have a parts repo: https://github.com/FourThievesVinegar/Parts/tree/master/v5 - What we need is an updated CAD file for the parts that includes this new hole.

sparklestheunicorn, 2024-04-25:
The v0.6 manifold core has many more holes than the previous reactor design. This is complete.

closed 2024-04-25 by sparklestheunicorn

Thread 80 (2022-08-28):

FourThievesVinegar/solderless-microlab #80: SPIKE: How do we get recipes onto the microlab?

sparklestheunicorn, 2022-08-28:
Currently, the process of adding a recipe to the Microlab is to copy a file onto the SD card or download it manually from the internet. It would be nice if there were a more integrated way to add a recipe, rather than "Get a file and put it in the recipes directory"

0x42red, 2022-08-28:
I imagine we could do the following.

Web GUI intakes recipe -> API validates it
The validation can check for the following
  - Does the recipe have the valid data in it
  - Does the recipe run
  - Does the recipe have an exit condition
  - Does the recipe break any safety bounds(temp probes are rated for N degrees and they want to use N+20)
  - additional thinking on this could be good

Once the code is created the GUI could send another API request to take that same recipe and return a flowchart for the user of the recipe. This will allow them to confirm the steps look how they expect.

Both of these steps can give a better UX but also prevent broken recipes from getting to users/being ran with runtime errors.  Additionally since recipes are live Python code instead of just JSON it might make sense to allow for simulation tests.  For example they can provide a list of steps and the selected decisions with the expected outcome.  This can allow recipes with branches to be quickly simulated instead of attempting to calculate all the permutations of a recipe.

myrinzic, 2023-01-17:
Leantime Ticket 31

closed 2024-04-25 by sparklestheunicorn

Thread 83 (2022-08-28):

FourThievesVinegar/solderless-microlab #83: Migrate to 3MF from STL for hardware files

0x42red, 2022-08-28:
Currently we use STL files for the 3d files.  We should export a 3MF version of the file for use instead.  With 3MF units of measurement are baked into the format so reproductions should be more accurate as well as some other features that might matter to the project in the future.

https://www.3dnatives.com/en/stl-vs-3mf-280620224/

0x42red, 2022-08-28:
@sparklestheunicorn in the log it looks like you made the last change to the STL.  Do we have access to the CAD project files still?  Would that make sense to also put them in the repo?

myrinzic, 2023-01-17:
Leantime Ticket 91

sparklestheunicorn, 2023-10-04:
Alas we do not have access to the original CAD files - they will need to be re-cadded.

sparklestheunicorn, 2024-03-06:
Parts have been re-cadded and [we now have](https://github.com/FourThievesVinegar/microlab-parts/tree/master/v5) both STL and STEP files

closed 2024-03-06 by sparklestheunicorn

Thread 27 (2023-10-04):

### ISSUE TITLE
Recipe details and descriptions

### ISSUE THREAD

**Issue by sparklestheunicorn** [FourThievesVinegar/solderless-microlab#27]
It would be nice for users if recipes had an ingredients list, and a short description so users can orient themselves before recipe preparation. Something like:

name: "aspirin"
ingredients: ["2.0 g salicylic acid", "XX mL acetic anhydride", "XX mL H2SO4"]
description: "A common pain reliever originally derived from willow bark."

This would also require a /details/<name> backed API end point (or equivalent) that returns details for a particular recipe.

To consider: do we also want to include common dosage and effect information?

**Comment by myrinzic** [comment]
Leantime Ticket 109

**Comment by sparklestheunicorn** [comment]
This is complete

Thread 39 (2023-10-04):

### ISSUE TITLE
Create hardware testing endpoints

### ISSUE THREAD

**Issue by sparklestheunicorn** [FourThievesVinegar/solderless-microlab#39]
Currently the backend doesn't have endpoints for testing relays or stepper motors. As a developer and user I would like them to exist.

Acceptance criteria:
- There exist endpoints on the python service to:
  - Test each of the relays one at a time
  - Test each of the motors one at a time
  - Test all of the relays in sequence
  - Test all of the motors in sequence
  - Get the thermometer temperature
  - Activate the stirrer (or is this just one of the motors?)

**Comment by myrinzic** [comment]
Leantime Ticket 101

**Comment by sparklestheunicorn** [comment]
This is now handled by using a built-in test recipe

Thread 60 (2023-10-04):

### ISSUE TITLE
Enable recipes to be written in more accessible formats and imported

### ISSUE THREAD

**Issue by sparklestheunicorn** [FourThievesVinegar/solderless-microlab#60]
Writing python classes is cumbersome and requires specialized knowledge. More accessible formats like markdown or csv would make recipe creation easier for end users, especially non-technical folks.

- [ ] Investigate formatting options and decide on reasonable formats (JSON?)
- [ ] Write functionality to import recipes from these formats
- [ ] Update Apothecarium to export the new format

**Comment by myrinzic** [comment]
Leantime Ticket 96

**Comment by sparklestheunicorn** [comment]
These are now JSON

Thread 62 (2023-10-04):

### ISSUE TITLE
Write startup scripts

### ISSUE THREAD

**Issue by sparklestheunicorn** [FourThievesVinegar/solderless-microlab#62]
We need scripts to run the backend and gui on startup on the pi.

- They should run at startup and start the GUI in fullscreen mode.
- If there are errors, they should raise them to the user in understandable ways.
 - Ideally we would recover gracefully.

**Comment by myrinzic** [comment]
Leantime Ticket 95

**Comment by sparklestheunicorn** [comment]
Startup scripts exist and the production disk image runs everything at boot and user login

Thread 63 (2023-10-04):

### ISSUE TITLE
Make a Disk Image

### ISSUE THREAD

**Issue by sparklestheunicorn** [FourThievesVinegar/solderless-microlab#63]
As a beta user, I want an easy experience setting up the microlab.

This is dependent on other beta Release issues being completed.

The image should start up auto-magically when the RPi is turned on with no configuration required.

The image should be uploaded to a public URL.

**Comment by myrinzic** [comment]
Leantime Ticket 93

**Comment by sparklestheunicorn** [comment]
Disk images are made and seeding

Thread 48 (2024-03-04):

### ISSUE TITLE
BACKEND: Backend keeps going after simulated recipe completes

### ISSUE THREAD

**Issue by sparklestheunicorn** [FourThievesVinegar/solderless-microlab#48]
When I complete the aspirin experiment using the test celery configuration, I see the backend daemon continue doing things. The gui gets 500 errors when this is happening. The status reverts to "running" after being "complete" for 2 polls.

This is happening in the simulation environment and seems to be related to heating steps.

![image](https://user-images.githubusercontent.com/2106250/123562534-439a4680-d77d-11eb-9239-21d08b89c950.png)

**Comment by myrinzic** [comment]
Leantime Ticket 100

**Comment by 0phelia36** [comment]
This was fixed at some point I think, and shouldn't be possible now in any case now that celery has been removed.

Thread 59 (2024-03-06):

### ISSUE TITLE
UI: Show status for individual steps

### ISSUE THREAD

**Issue by sparklestheunicorn** [FourThievesVinegar/solderless-microlab#59]
As a microlab user, I want to know what's happening with the microlab when I'm running a reaction. I want to have a timer that counts down the remaining time in my step. I want to know the temperature (for example) when the heat is being adjusted.

Acceptance Criteria:
- There is a temperature readout on the status page
- There is a countdown when the steps are timed

**Comment by myrinzic** [comment]
Leantime Ticket 29?

**Comment by sparklestheunicorn** [comment]
This is now supported.

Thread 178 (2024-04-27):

FourThievesVinegar/solderless-microlab #178: As a user and Developer, I want the HDMI and small display to both work at the same time

sparklestheunicorn, 2024-04-27:
Currently when you install the LCD drivers they disable the HDMI port. It's not clear how to un-do that. Technical research on the feasibility and approaches would be really great.

phaseloop, 2024-09-08:
I did similar research some time ago. TLDR: It's ugly, hacky, difficult, board dependent and may bring more problems than needed:
The only solution I found:
https://forums.raspberrypi.com/viewtopic.php?t=306624

Raspberry PI becomes a liability due to their politics and pricing. There are now more powerful and cheaper alternatives.

As far as I see you use 4-5 GPIO ports to control relays. This can be moved to CNC shield as CNC controllers (grblHAL included) support M64-M65 commands which are used to control additional GPIO pins on the board (exactly for scenarios like that).

So technically -  a next version could just wire all IO and motors to CNC shield (whatever board is supported by grblHAL) and just expose USB ports/hub. Then you use whatever PC/laptop/Intel N100/raspberry you have.

This essentially halves the cost of microlab controller because you can repurpose any computer laying around and gathering dust instead of buying raspberry (which I remind is prone to semiconductor shortage and delivery problems as it happened during covid).

sparklestheunicorn, 2025-10-20:
DSI port is how we recommend people do it now.

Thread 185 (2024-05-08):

FourThievesVinegar/solderless-microlab #185: PARTS: As a user I want different or expanded BOMs for different regions of the world

sparklestheunicorn, 2024-05-08:
Currently the Microlab BOM is written by and for audiences in the US. Replicators in the EU have reported difficulty obtaining certain parts and needing to use replacements. It would be nice to capture a variety of alternatives folks have used to make it easier for everyone.

sparklestheunicorn, 2024-09-09:
Potential [duplicate of this issue](https://github.com/FourThievesVinegar/solderless-microlab/issues/244). Leaving them both for now, but closing one probably means we can close the other.

phaseloop, 2024-09-10:
I did a review of BOM - except mason jars nothing seems extraordinary for EU market (most of stuff in BOM sourced from Aliexpress anyway).

1/4'' copper pipe can be replaced with 6 mm copper pipe metric standard.  Barbed tee fitting from McMasterCarr is available in most construction shops (think HomeDepot) on garden section or in motorcycle shops (for fuel lines probably).

If you can check in user reports what parts were troublesome, I could give some guidance.

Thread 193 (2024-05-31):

FourThievesVinegar/solderless-microlab #193: Research alternatives to copper coil heat exchanger

sparklestheunicorn, 2024-05-31:


phaseloop, 2024-09-08:
Silicone hose wound around 3d printed frame and secured with zip-ties? Popular in helix RF antennas:

https://www.thingiverse.com/thing:4980180

Thermal conductivity of silicone is like 800 times worse than copper but it's cheap and easy to make so maybe in this application it can be a "good-enough" trade-off.

While I suppose biggest pain-point of copper coil is actually winding it - maybe 3d printed frame + thin copper brake line can be a good and easy way to do it.

Unless there is a different need to get rid of this heat-exchanger.

phaseloop, 2024-10-28:
Removing need for a heat exchanger: https://github.com/FourThievesVinegar/solderless-microlab/issues/276

sparklestheunicorn, 2024-11-07:
We're already concerned about efficiency losses from the copper, so moving to silicone probably isn't the move. There are also automotive aluminium heat sinks (~1/2 the heat conduction of copper) that are pretty cheap and available. Honestly, bending the coil around a cylindrical jig isn't that hard, but it would be nice to have other options. 

Directly heating the jacketed region as suggested in #276 would be great if we can get it working :+1:

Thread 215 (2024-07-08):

FourThievesVinegar/solderless-microlab #215: SPIKE: PARTS: As an assembler, I want to know whether DIY peristaltics are good and which ones are best.

sparklestheunicorn, 2024-07-08:
At ~$30/ea in 2023, the three peristaltic pumps are a major part of the cost of the MicroLab. In addition to being costly, they are also relatively limited in terms of the number of vendors selling them to the public. It would be good to look into alternatives and their reliability.

There are a number of 3d-printed peristaltic pump designs out there ([one example](https://www.myminifactory.com/object/3d-print-peristaltic-pump-63137)). An exploration of the various options and tests of their reliability would be helpful in deciding whether we think we want to encourage our users to go with printed pumps, and if so, which ones?

phaseloop, 2024-10-10:
Here is the curated list of available pump designs from thingiverse and printables.

**Also it's worth considering a different approach - pressing a syringe cylinder to extract given volume of liquid instead of pulling it using pump.** The downside of it is the limit of syringe volume while with pump we can connect anything to the input side.

Used assumptions:

- no print-in-place designs, they need good printer tuning and tolerance. Also when they fail you probably need to print a new one from scratch.
- only pumps using steel bearings as pressure elements to have as biggest MTBF as possible and build consistency (i.e pump calibration being a bitch)
- pump form allowing it to mount/adapt it to microlab. No standalone big pumps or weird designs
- stepper motor pumps only, no weird steppers - only Nema 17.
- as simple to print and build as possible - no planetary gears, etc.

**Pump designs**

**Editor's choice!**

- https://www.thingiverse.com/thing:4692199

Heavy-duty, well designed pump with adjustable hose tension. Includes source scad files for further modifications (no other design on the list probably does that).

Uses 6 mm tubing.

**Other**

- https://www.thingiverse.com/thing:4255438

Easy and nice design - uses 3 mm tubing. Pump intake seems to be integrated into housing (??) which seems to be weird.

- https://www.myminifactory.com/object/3d-print-peristaltic-pump-63137 

(OG design linked in this issue)

- https://www.printables.com/model/248041-growflow-nema-17-peristaltic-pump

Similar design but uses less popular needle bearing

- https://www.thingiverse.com/thing:1134817

Nice and secure design but needs some minor fixes to tube guide to prevent it from moving and keep the precision.

- https://www.printables.com/model/818373-nema-17-peristaltic-pump-water-pump-measuring-pump

ok-ish but tube seems to not be secured properly and there is a risk it will fall out during operations

- https://www.printables.com/model/129756-peristaltic-pump-nominal-diameter-o8mm-for-fluids-

ok-ish but the bearing mount gives me anxiety and I doubt it will work more than 10 minutes. Someone tried to adapt aluminium pump to 3d printing.

- https://www.thingiverse.com/thing:3346506

Easy and clean design but risk of tube falling out

- https://www.thingiverse.com/thing:3109449

Nice and clean design but bearings are not secured with screws and keeping pressure between pump rotor and motor shaft is the single point of failure.

sparklestheunicorn, 2024-10-13:
Thanks @phaseloop! We're running this by some of the CAD design folks.

phaseloop, 2024-10-13:
I have a pretty long and solid experience in FreeCAD - I would love to join discussions if that's possible.

sparklestheunicorn, 2024-10-21:
@phaseloop please drop us an email at volunteerⒶfourthievesvinegar.org and we'll put you in touch.

with-eight-hands, 2024-12-19:
Thank you phaseloop for compiling this list!

I have tested https://www.thingiverse.com/thing:4255438 and found it to be simple and relatively functional. Comments:
- The barb connector inlet/outlet is not required; the design can be used with one continuous piece of tubing.
- The bearings aren't quite wide enough for the specified tubing. (The tubing becomes wider when squished flat.) It is more reliable if the middle part of the rotor is flipped so that the bearings are in pairs directly adjacent, used for a single tube.
- Inserting the tubing and rotor relies on the tubing being quite stretchy. To accommodate stiffer tubing (e.g. PTFE), it would be better to have slots rather than holes on the side of the housing.

with-eight-hands, 2024-12-22:
I made a pump design inspired by the design linked above. It uses pairs of bearings to accommodate tubing with flattened widths up to 8 mm, and it has slots so that tubing stretching is not necessary. The amount of tube compression is changed by varying the distance from the center to the bearing mount holes. (This isn't very clever, but it keeps the design simple.) I have tested it with PTFE tubing (11G, 2.41 mm ID, 3.01 mm OD) and silicone tubing (3 mm ID, 4 mm OD) and it seems to work OK.

[image]

STL files here include parts for rotors with dimensions that yield 0.55, 0.70, or 0.85 mm clearance between the bearings and housing walls. 0.55 mm clearance worked reasonably for PTFE tubing with a nominal 2\*wall_thickness of 0.60 mm. 0.85 mm clearance worked for silicone tubing with a nominal 2\*wall_thickness of 1.0 mm.

[pump-prototype.zip](https://github.com/user-attachments/files/18222714/pump-prototype.zip)

phaseloop, 2024-12-23:
Cool! Have you seen the design uploaded recently? It also uses pair of bearings.

https://github.com/FourThievesVinegar/microlab-parts/tree/master/peristaltic-pump

We could really use a feedback on that design, especially about what you are writing about teflon tubes - maybe we can use what's best from both of them.

with-eight-hands, 2024-12-23:
Oh, I did not. Very nice! Unfortunately I won't be able to do more prototyping any time soon, but I can give some impressions.
- Overall I expect that should work fine with teflon tubing, given the right spacing. Changing the bearing assembly dimensions like I did should work fine.
- The swing-away design looks like it could be easier to load than the design I used, which requires some awkward sliding.
- Having the top bracket fixed onto the design has a downside: you must fish the end of the tube through the pump in order to load and unload it. If the tubing has been used with chemicals, you will need to clean the tubing or carefully cover the ends before unloading in order to avoid contamination. Poor chemical hygiene is bad for tools as well as bad for people (even a tiny drop of hydrochloric acid from mostly empty tubing can cause horrible rusting). I suppose for this design that just means unscrewing the housing / top bracket during every load and unload, which isn't too big a problem.

Overall it looks like slightly more work to assemble and to load the tubing (assuming we are not passing the tubing end through the pump), but I'd guess it should work OK, even with teflon.

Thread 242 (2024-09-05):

FourThievesVinegar/solderless-microlab #242: [BUG] Permission Denied to /etc/microlab/microlab.ini

zenny, 2024-09-05:
Hi,

Thanks for posting an interesting repo.

Trying to build a development server to try with `python3 main.py`.

```
$ python main.py
Traceback (most recent call last):
  File "/home/user/Downloads/solderless-microlab/backend/main.py", line 11, in <module>
    import config
  File "/home/user/Downloads/solderless-microlab/backend/config.py", line 125, in <module>
    microlabConfig = MicrolabConfig()
                     ^^^^^^^^^^^^^^^^
  File "/home/user/Downloads/solderless-microlab/backend/config.py", line 24, in __init__
    makedirs(path.dirname(configFileName), exist_ok=True)
  File "<frozen os>", line 225, in makedirs
PermissionError: [Errno 13] Permission denied: '/etc/microlab'
```

Since the entire build was built as a user permission, why running the `main.py` searches for an inaccesible config in `/etc/microlab/microlab.ini` making it unsafe? I could not find `microlab.ini` examples in this repo either.

Cheers,
/zenny

sparklestheunicorn, 2024-09-06:
In current production environments (on a RPi), running the python script using sudo is necessary to access the GPIO pins, so that's the way the software and scripts have been designed. We have made some efforts to make everything run as a regular user, but it hasn't been high enough priority compared to other recent features and release activity.

I'll leave this open until we (a) figure out how to remove the need to run the backend scripts as super user or (b) determine that's the only way to do things and see if there's a workaround for development on non-pi machines.

zenny, 2024-09-06:
> In current production environments (on a RPi), running the python script using sudo is necessary to access the GPIO pins, so that's the way the software and scripts have been designed. We have made [...]

@sparklestheunicorn Thanks for the reply.

What I assigned the ownership of the following directories to the user as an alternative way than using `sudo` itself:

```
sudo mkdir -p /etc/microlab
sudo chown -R $USER:$USER /etc/microlab
sudo chown -R $USER:$USER path/to/this/repo/backend/env
sudo chown -R $USER:$USER /var/log/microlab
sudo chown -R $USER:$USER /var/lib/microlab
```

to make $USER to run the script, but not ideal, imho, securitywise. 

Thanks for the wonderful work and look forward to changes you are planning to overcome the bottleneck. 

Cheers,
/zenny

sparklestheunicorn, 2025-09-09:
This should be resolved with the new imager repo

closed 2025-09-09 by sparklestheunicorn

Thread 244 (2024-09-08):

FourThievesVinegar/solderless-microlab #244: PARTS: As non-US user I want to use non-mason jar glassware

phaseloop, 2024-09-08:
Outside US, mason jars are either not available, available in limited size choice or way overpriced. This makes building microlab much more difficult or impossible (depending on region/country).

Solution: Create a 3D adapter to use regular ("European style" [?]) jars - those are used to package food and are available worldwide even as recycled glass. Standardized lid diameters are 33, 43, 53, 59, 66, 77, 82, 100, 110 mm. Outside jar should use 82 mm which is most popular (need to decide internal one diameter).

**Note:** Non-mason canning jars used in US (judging from the photos) use different thread sizes and lids than the rest of the world

The issues with regular jars are:

- there is no "neck" below lid as in mason jars so there is no way to attach them to the device using flange.
- lids are made of carbon steel and are heavily prone to rusting once internal plastic coat is damaged - so cutting a center hole for reactor manifold lid is not an option (aside of that - it's pain in the ass to cut).

Solution: 3D printed jar lid (adapted to thread which I believe is ISO standardized for jars) - with center hole matching reactor manifold and external features allowing it to work with flange and hand the jar on the device. If not - separate flange should be designed to match lid features that in tandem allow this to secure jar in the device.

This issue will evolve - I'll try to design those lids in CAD but I have ADHD and focusing problems so I'll be really thankful for someone to respond here once in a while and remind me of it. Any feedback is welcome - I love what you do!

phaseloop, 2024-09-08:
Edit: I'm looking at the photos of the device and I see that jar is standing on a table next to the microlab. Can someone here say what is the role of a flange here?

sparklestheunicorn, 2024-09-09:
This looks like a potential [duplicate of this issue](https://github.com/FourThievesVinegar/solderless-microlab/issues/185) (but with more detail :+1: ). Leaving both open for now and linking them.

We had a replicator in the EU produce another manifold for jars available there. Since then, we have redesigned the manifold however, so it might be good to choose appropriate jars for the European market, and [localize this directory](https://github.com/FourThievesVinegar/microlab-parts/tree/master/v6).

This would mean (to start) creating a new `europe` subdirectory in the `v6` directory, and creating any adapted part files there. We would also want a list of localized off-the-shelf parts added to a new tab in the parts list spreadsheet for each market. 

Finally, we would need to add an addendum document for each new region and mention them in the appropriate places (when discussing sourcing the parts and prominently in the documentation for any module that requires modifications.

phaseloop, 2024-09-18:
An update - co called "2030 type thread" most popular in jars around the world is awful to model for 3D printing because the short and thin plastic thread in hot environment will not be reliable at all. Maybe there is a way to attach the lid different way - but in the meantime I've designed manifold lid to be used in "Weck" system jars - secured by metal clamps used by default in this system.

While Weck jars and not exactly the cheapest ones - they are much more popular across the world. AFAIK reactor core can be adapted too to Weck system when a matching set of jars is found.

System picture for reference. After some testing I'll post the PR with the lid.

[image]

with-eight-hands, 2024-12-19:
See #292 for an example using a media bottle with DIN GL45 threads as the inner vessel. 3D-printed threaded lids seem to work fine with this thread profile. Wider threaded mouths are defined in the same standard, but they are less commonly available, so the outer vessel may require a different solution.

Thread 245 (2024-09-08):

FourThievesVinegar/solderless-microlab #245: Microlab should be independent from Raspberry PI

phaseloop, 2024-09-08:
I extracted part of my comment from #178 because I think it deserved another issue:

Raspberry PI becomes a liability due to their politics and pricing and recent versions become more expensive than a regular mini-pc. There are now more powerful and cheaper alternatives.

As far as I see microlab uses 4-5 GPIO ports to control relays. This can be moved to CNC shield as CNC controllers (grblHAL included) support M64-M65 commands which are used to control additional GPIO pins on the board (exactly for scenarios like that).

So technically -  a next version could just wire all IO and motors to CNC shield (whatever board is supported by grblHAL) and just expose USB ports/hub. Then you use whatever PC/laptop/Intel N100/raspberry you have.

This essentially halves the cost of microlab controller because you can repurpose any computer laying around and gathering dust instead of buying raspberry (which I remind is prone to semiconductor shortage and delivery problems as it happened during covid).

0phelia36, 2024-09-10:
I'm going to take a look into adding software support for controlling gpio pins via grbl. The microlab can already be independent from the raspberry pi specifically if you install the microlab software yourself on another SBC, and create a config file for the SBC you're using. We've created a file for the the librecomputer potato that you can see [here](https://github.com/FourThievesVinegar/solderless-microlab/blob/master/backend/data/hardware/controllerhardware/AML-S905X-CC-V1.0A.yaml) that could be used, and can be referenced if anyone wants to try this with another raspberry pi clone.

phaseloop, 2024-09-10:
Thank you, I didn't know that.

As for grbl - while only newer grblHAL (for 32 bit boards) support "native" pin control, with older arduino + CNC shields it would be possible to use pins and commands used for coolant pumps and laser air-assist (M7/M8/M9 commands for example) - then just wire microlab relays to those pins.

I have a background in electronics and CNC so let me know if you need any help :).

0phelia36, 2024-09-12:
I think that only gives 3 pins though? At least with the cnc shield we're using. Unless I'm missing something there's: spindle enable + spindle direction + coolant enable. I tried it out on mine and M3 and M5 didn't seem to change the state of spindle enable either, so really only 2, which would not be enough to be the only source of gpio ports for running the microlab.

michal-rogala, 2024-09-13:
Can you try "M3 S10000"? - grbl usually does not enable spindle power without complete speed settings.

M7 command for coolant pump mist is by default disabled in BRBL - it should drive pin A3 (or A4/A5) even if it's not exposed on CNC board - it's available on the underlying board.

Should be not a big problem to make a compiled version of grbl (with enabled M7) and share on github to just flash the board and not bother users with firmware compilation anyway.

phaseloop, 2024-09-13:
Can you try "M3 S10000"? - grbl usually does not enable spindle power without complete speed settings.

M7 command for coolant pump mist is by default disabled in grbl - it should drive pin A3 (or A4/A5) even if it's not exposed on CNC board - it's available on the underlying board.

Should be not a big problem to make a compiled version of grbl (with enabled M7) and share on github to just flash the board and not bother users with firmware compilation anyway.

0phelia36, 2024-09-15:
"M3 S10000" also doesn't work, the spindle enable pin just stays high. Tried it also with "M3 S0", "M4 S0", and "M4 S10000", with every one of those followed by M5 and nothing changed the state of the pin. M3 and M4 are changing the state of spindle direction. Not sure what the issue could be with spindle enable.

phaseloop, 2024-09-16:
It may be in "laser mode" when the laser only gets enabled when x/y axis are moving to avoid fire risk of laser stopping and burning a hole through the table.

Can you dump the config using `$$` ? Also you can try if `$32=0` command changes the behaviour.

0phelia36, 2024-09-17:
$32=0 also didn't change anything.
Config:

> 
> $$
> $0=10
> $1=25
> $2=0
> $3=0
> $4=0
> $5=0
> $6=0
> $10=1
> $11=-0.000
> $12=0.002
> $13=0
> $20=0
> $21=0
> $22=0
> $23=0
> $24=25.000
> $25=500.000
> $26=250
> $27=1.000
> $30=1000
> $31=0
> $32=0
> $100=250.000
> $101=250.000
> $102=250.000
> $110=240.000
> $111=240.000
> $112=240.000
> $120=10.000
> $121=20.000
> $122=10.000
> $130=200.000
> $131=200.000
> $132=200.000
> ok

phaseloop, 2024-09-17:
Ok, I've reviewed the grbl source code and the mystery is solved why spindle enable pin is always 5V.

There is a mismatch between CNC shield design and newer grbl versions for the sake of spindle speed control. Real spindle enable pin is now the "Z+" endstop on the board. This can be easily changed back in config.h.

As grbl is not developed anymore (replaced by grblHAL for 32 bit boards) and it only supports 328p microprocessor anyway, we can safely fork their repository - change default configuration to match desired behaviour, release precompiled .hex file for people to download instead of making them compile it.

Should not be that hard later to gut some unnecessary code (as we don't do CNC anyway) to make some space in flash and implement M65 code to toggle more pins - like Y+, X+, Hold, Resume, etc.

This would be forward compatible if the future microlab will switch to grblHAL CNC boards when they became cheaper and more popular (which already happens) - as those boards already implement M65 and pin maps as outputs to control.

0phelia36, 2024-09-20:
Is that something you're capable of and interested in doing? That's outside of my skillset and capacity to work on at the moment, but I think would be good to have. Having all the gpio control done through the arduino would make it much easier to support other SBC's with the current build since we wouldn't need to go through creating config files for each one.

phaseloop, 2024-09-25:
Yeah, I can do it. We need to solve one issue in the meantime - how to easily connect relay pins to the CNC board holes like spindle enable, Y+, etc. As soldering is a no-no - I guess there needs to be another way.

0phelia36, 2024-09-26:
Cool, I've forked grbl [here](https://github.com/FourThievesVinegar/grbl) and have given you access to the repo. And unless I'm missing something I don't think the connections between the arduino and the relays would have to be any different than current connections between the pi and the relays?

phaseloop, 2024-09-26:
Thanks!

Yeah, you're right - I used to work with some really old CNC shield design, I see newer versions have proper pin headers in a row, so that solves a lot of issues.

0phelia36, 2024-10-15:
Yeah I can test it, though I won't be able to until probably this weekend.

0phelia36, 2024-10-21:
I tested it and everything seems to work fine, so I'm going to work on adding support in the microlab for it

0phelia36, 2024-11-28:
@phaseloop PR #282 adds control of gpio pins through grbl. You can use the arduino-only-no-SBC controller hardware file in that PR to test only using the arduino, though our version of grbl will need to be modified to add a 4th pin, it currently errors trying to setup the nonexistent fourth pin. If you change the "BCM_26: 4" line in that file to to "BCM_26: 3" then you can test that the pin control is working, though the 3rd pin will be behave strangely since two different things are then controlling it.

sparklestheunicorn, 2024-12-17:
This may not work for our purposes but adding it here in case anyone wants to investigate the option of using an old Android smartphone instead of a SBC: https://hackaday.com/2024/12/16/using-a-smartphone-as-a-touchscreen-for-arduino/

phaseloop, 2024-12-23:
@0phelia36 - Thanks, I implemented pins 4 and 5 in GRBL (spindle enable and direction). I need to test it and I'll create a new grbl release.

phaseloop, 2025-01-04:
@0phelia36 - I just released grbl v0.0.2 -we now support pin 4 and pin 5 too

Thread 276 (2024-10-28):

FourThievesVinegar/solderless-microlab #276: PARTS: Use small ceramic heater and limit fire risk of running heat exchanger

phaseloop, 2024-10-28:
Most common failure mode of a relay is being stuck in "closed" position. 

Having 500W water heater in a small jar is a big fire risk - in case something goes wrong (relay or software issue) heater will evaporate water fast and then start to melt itself and surrounding parts, starting fire.

An alternative is to use small ceramic heater used in 3D printers (cost is $3-6). Heater powers range from 20 to 100W and after simple waterproofing it can be submerged in the outer reactor jar. In case something goes wrong - heater has contact only with non-flammable wire insulation and glass and will burn through heating material and stop working before doing more damage.

There are also significant benefits to this solution:

- reduced fire risk (as mentioned above)
- simplified build time and BOM as hot side heat exchanger is not needed anymore
- not relying on mains voltage and being able to run microlab off battery or small power inverters
- possible better efficiency than heat exchanger

Keeping hot side circulation pump is a matter of some tests and discussion - whether water mixing to distribute heat around jar is needed or regular heat convection will be enough.

sparklestheunicorn, 2024-11-07:
An example [product link](https://www.amazon.com/dp/B07YFBRKZ4). Seems like waterproofing and general heating effectiveness are the main questions here.

phaseloop, 2024-11-08:
Effectiveness can be improved easily by making a ring out of copper pipe (from heat exchanger) and putting the heater inside the pipe on one end. I suppose 6 mm heater diameter is just right for it to fit.

dallinbeutler, 2025-02-07:
apparently brewers use  this [immersion heater ](https://www.amazon.com/DERNORD-Immersion-Cartridge-Heater-Tublar/dp/B0BC752LPS?pd_rd_w=pHuoS&content-id=amzn1.sym.cd152278-debd-42b9-91b9-6f271389fda7&pf_rd_p=cd152278-debd-42b9-91b9-6f271389fda7&pf_rd_r=EK8MB96SZMRG5S327DK7&pd_rd_wg=BidcH&pd_rd_r=786f6788-8a1f-41ea-aef4-292a8957afac&pd_rd_i=B0BC752LPS) made of stainless steel that could be part of the reactor core stirring lid insert and be an easy plug n play 

cheaper, but more work would be a [ptc heater](https://www.amazon.com/Heating-Thermostat-Element-Temperature-Resistant/dp/B07VWP5LLJ?crid=3CYKN0R0SLA9T&dib=eyJ2IjoiMSJ9.hWinpmcqSU--3l81wofUxjkJqYWFLJil2yiQmMpg4ebTRqirZuHhcn8IzUG-nrPTyTQh5NDd0fJsL1mboLozBpqD07m7nHYrK2XyukMlpZZHA3j-a0P7u5-wtDelv_nN3L0SdHVub54Xou0au5DEXjTKyJ9eaEcktmiE0WEXkqstjUNB6SK7pMPlgDot7KLUwLZzNjniM82I5JkkZ6baeIOfnayyb21RuhXXZ48MGtGBJ0ouMLMVPiuza1J4qDdxfYMu4lRagK_LQzvvzldM0arfjOrRsRhOWKnt6xPV5smFzDIWOzkwJGu6iwcVihsYzt4moLDv6YlF7MjGd2BP1BBHv36JOD8IZKGPXSxRtvJp2MGonvB0N3gTm4CMUELeyc41oVtgb6whXOCJuL7qjljI3rjBXibe2R_d4Bn5Z_90CNFCsnerrVl3cFFPr3K7.hdSdtWQsyqbv49UPU6Sune4K--Wj6KuLQdpuvD0bv6A&dib_tag=se&keywords=ptc+heating+element+12v+waterproof&qid=1738910101&sprefix=ptc+heating+element+12v+waterproof%2Caps%2C113&sr=8-24#customerReviews)  with the added benefit of automatically shutting off at specific max temp depending on the component.
as for waterproofing, could protect it with a high enough temp plastic sleeve of a sort, and inserting it directly in the outer circulation bath

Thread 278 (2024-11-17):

### ISSUE TITLE
Two important links dead on setup and operation page 

### ISSUE THREAD

**Issue by abstractzwieback** [FourThievesVinegar/solderless-microlab#278]
On the [setting up and operating the microlab](https://github.com/FourThievesVinegar/solderless-microlab/blob/master/docs/operation.md) page the two below links are dead. I don’t know the project well enough to know what these are meant to point to. 

[Control Unit](https://github.com/FourThievesVinegar/solderless-microlab/blob/master/docs/assembly-control-unit)
[MicroLab Cables](https://github.com/FourThievesVinegar/solderless-microlab/blob/master/docs/assembly-control-unit#cables)

**Comment by sparklestheunicorn** [comment]
Thanks for reporting this. It should be fixed now :+1:

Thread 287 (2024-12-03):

FourThievesVinegar/solderless-microlab #287: Can't run the backend with docker

suspiciousRaccoon, 2024-12-03:
heya!

I tried running the project with docker but there are a few problems.

1.  `TypeError: 'type' object is not subscriptable`
This is the first error I encountered. A quick google [search](https://stackoverflow.com/a/63460173/21430041) led me to this problem originating from the type hints. Older python versions had a different API, so they're not compatible with the dockerfile's python version. Upgrading the python version to 3.10 fixed this.
2. Missing dependencies
`backend/api/`

0phelia36, 2024-12-04:
Hello! Thanks for the issue. 

The gpiod error you're running into is due to the fact that gpiod is not supposed to be installed via pip at the moment and instead has to be installed as a system package via apt to be used using `sudo apt install python3-libgpiod`. If you're just trying to run the code for development or testing you can instead go into the frontend, go to settings, and change the value of the lab hardware config dropdown to "simulation-pi" and that error will be avoided as it won't attempt to import and use gpiod to control the state of the gpio pins, and will instead use stub functions for gpio control that basically do nothing.

I don't think anyone has run the project with docker in a while so it might take some work to get that fully running, at the very least the docker-compose file will need to add volumes mounted for /etc/microlab and /var/lib/microlab for the microlabs configuration and recipe data to persist, not sure if there's anything else that's changed that might cause issues.

phaseloop, 2024-12-04:
I'll try to run it and fix those errors. @suspiciousRaccoon this "No such file or directory" error may be caused by GPIO device being unavailable. Are you running this on raspberry? If so - did you enable raspberry GPIO support/driver and uncomment docker-compose path mapping?

phaseloop, 2024-12-27:
Will be fixed by https://github.com/FourThievesVinegar/solderless-microlab/pull/296

phaseloop, 2025-01-06:
@suspiciousRaccoon  - please test the fix (merged to main) and close the issue or report other bugs if you find them. Thanks :)

suspiciousRaccoon, 2025-01-10:
Hi!

Sorry for taking a while. I found a tiny issue but it should be fixed by #303. That aside, docker seems to work! c:

closed 2025-01-10 by suspiciousRaccoon

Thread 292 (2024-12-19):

FourThievesVinegar/solderless-microlab #292: Use materials with better chemical compatibility (teflon and borosilicate) for the inner reactor vessel (prototype included)

with-eight-hands, 2024-12-19:
[Please let me know if there's a better place to put things like this!]

The current design has the reactor contents in contact with a mason jar (soda lime glass) and the 3D-printed reactor core (probably PETG or PLA). This is undesirable because the reaction mixture may degrade these materials, causing mechanical failure (bad) or contamination of the reaction mixture (even worse). From a safety perspective, I believe this should be a priority, and based on some preliminary work, I think this is achievable in the near term.

Avoiding soda lime glass is straightforward; simply use the lab equivalent of a mason jar. Borosilicate media bottles are widely used for chemical storage and rated for autoclaving. They are available with a DIN-standard screw profile (e.g. GL45), so designing new lids isn't too hard.

Avoiding 3D-printed parts in contact with the reaction mixture involves slightly more effort. PTFE (Teflon) is one of the few polymers that is compatible with most common lab chemicals. It is easy to machine, but conventional machining might be considered inaccessible for many users. Luckily, similarly to how the classic mason jar lid design is separated into two parts, a reactor lid can be designed around a simpler PTFE disc and a more complex 3D-printed screw closure that connects to the external vessel and the motor. The minimal PTFE design would require cutting the circular outline and drilling 4 holes (1 for the stir rod and 3 for the reactants). Because the sealing* surface is the bottom face of the disc rather than the edges, the circular outline does not need to be precise and can be cut with a hacksaw. The holes for the reactant tubing do not need to be precisely located or angled and can be drilled by hand. The stir rod hole is the most critical. It should be perpendicular and centered, so would ideally be done with a drill press, but there is likely enough wiggle room for hand drilling.

I made a prototype based on the above ideas. The bottle (~10 USD), PTFE (~10 USD), and filament (~5 USD) represent pretty modest costs. Media bottles are also more commonly available internationally, partly resolving #244 . As you can see the PTFE disc outline is quite rough, since I cut it by hand, and yet that doesn't impact performance in any way. The glass/PTFE contact happens on the lower surface of the disc, not the edges.

[image]

[image]

The single 3D-printed piece clamps the PTFE disc to the bottle.

[image]

It also provides the motor attachment and flange to clamp to the outer mason jar.

[image]

[image]

Remaining issues:
- The choice of GL45 necks limits the room to work. Addition of glassware adapters or more than 3 reactants could be tricky. I don't see this as a major concern. GL80 media bottles (25 mm wider) exist, but they are harder to find especially for bottles <500 mL.
- The operating temperatures and safe ramp rates are still limited by the 3D print material and the outer mason jar. Replacing the outer mason jar may be feasible (especially if it doesn't need to be transparent), but making the screw-thread assembly without 3D printing or conventional machining might not be realistic.

Hopefully this gets other people thinking about how we can make this apparatus safe to use. I personally think this approach is accessible.

*Please don't try to do chemistry in a fully sealed glass vessel! Unintentional bombs are no fun.

with-eight-hands, 2024-12-19:
Here's the STL of prototype printed adapter. I might upload the FreeCAD source after some tweaks.

[GL45-to-mason-with-motor.zip](https://github.com/user-attachments/files/18203594/GL45-to-mason-with-motor.zip)

phaseloop, 2024-12-23:
Hey! I've been gathering concepts for the redesign of reactor manifold and your idea is really cool.

I suppose GL45 is the way to go, but we need to keep reagent tubes diameter pretty large - otherwise part of reagent volume will stay there (as in capillary tubes).

As for PTFE disk - do you think 3d printing a ring with special shape and wrapping it with PTFE tape would work too? There would not be holes for hoses but rather pockets around center hole so it's easy to wrap a tape around it.

As for outer jar - so far it seems we need to stick with "regional" variants - like mason jar, Weck system, etc. While it's impossible to 3d print a lid for an "european" jar, I'm experimenting with drilling center hole in a metal lid using step drill and secure the rest of the manifold using screws. And using GL45 as iron standard for a reactor solves a LOT of issues ;).

with-eight-hands, 2024-12-23:
Hmm. I'm not convinced that we need to keep the reagent tube diameter pretty large. Normally for a design like this, the reagent volume will be filling the tubing, and you would only start measuring after the line is primed, i.e. once the tube has been filled all the way up to the reactor entrance. If anything, tubing too large could result in space for air bubbles and uncontrolled flow. Larger tubing also means that we require more reagent solution just to operate the pump, which seems like a bad thing to me. The reagent in the line can potentially be pumped back into the syringe and recycled (although this is not good lab practice!), but it puts a lower bound on the amount of reagent you need to have regardless of how much you need for the reaction. As far as I know, no one has elaborated any target reactions for the microlab, but generally if we're thinking of reaction mixture volumes <200 mL, that's probably <10 g of reactants and products. So, it seems a bit silly to require twice that just to fill 30 cm of tubing. Also, 3 mm is about the largest flexible PTFE tubing that I could find.

Personally, I would not mess with wrapping a ring/disc with teflon tape. Teflon tape doesn't adhere to itself. If it is being clamped from all sides, it can form an OK seal, but the tension just from being wrapped won't prevent solvent vapors / splashes from working between the layers. I also imagine that the wrapping would become looser over time with loading and unloading. Maybe I am being a little obnoxious about the chemical compatibility stuff, but it seems like lots of people here haven't actually starting thinking about the chemistry part. I can't tell other people what to do, but I would absolutely try to avoid even incidental contact of heated solvents with random plastics in anything I might consume, even if it meant 20 hours of extra work. In this case, the effort to produce the lid that I made was probably <30 min, so to me it is an obvious choice.

A bit of an aside, but I was recently playing with cutting 8-mm teflon with a kitchen knife. So, you might not even need a hacksaw to approximate the teflon disc.

For the outer jar, I don't have any great solutions, but I do wonder about other attachment methods. I have thought about using french press coffee maker inserts. They're borosilicate, about the right size, and pretty available. I was wondering if a 3D print press-fit around the lip of a french press insert would be robust enough. It doesn't really need to seal or even sustain much force if the glass is supported from the bottom rather than suspended from the lid. Actually, one concept is how some french presses use a metal or plastic frame around the glass part, and the lid connects to this frame for a tight connection:

[image]

The print volume scares me a bit, but I guess it's not really larger than the 3D-printed stand.

I like your idea of modifying a metal lid, because it starts to resolve the issue of 3D print stability at high temperatures. I would love to replace the GL45 threaded part with something metal. Then, we're not limited to 80 C or whatever PETG can handle.

phaseloop, 2024-12-24:
Yeah, what you wrote about tubes and PTFE seal makes sense. I think it's good that you're vocal about chemical compatibility issues. I also suppose it will be possible in the future to design a 3d printed jig to help cutting PTFE seals.

While we are discussing french press glass - why not use a regular beaker? Then we can match expected reactor bottle volume to beaker volume to get close match and less thermal inertia (we're redesigning heating and power budget for a heater is pretty strict).

Technically we would not need any printed frame around it - only some kind of parametric fixture on top to match manifold to different beaker diameters and keep heater power lines in place.

Microlab v6 has the reactor hanging above table but I don't suppose this is necessary - it just needs to have thermal insulation and probably be placed inside some part to restrict movement or accidental toppling.

As for modifying a metal lid - I don't recommend that unless it's a last resort. Lids corrode awfully fast (at least jar lids).

GL45 thread could be printed on SLA printer in resin for high temperature performance (and/or printed in commercial facility on metal/nylon, etc) and then attached to the rest - printed cheaply in PLA/PETG.

with-eight-hands, 2024-12-29:
Oh, a 3D-printed jig for preparing PTFE is an excellent idea! A very simple thin template would be sufficient for most of the x-y placement, and a tube upward around the center hole location would help the stir rod hole be perpendicular without a drill press.

A beaker could make sense. I was thinking of French presses because some of them have the spout integrated with the lid, rather than as part of the glass. The lip of the glass vessel for this kind is a flat circle, which would work better with a press-fit reactor lid. But yes, if the spout is covered by part of the print or maybe even just with aluminum foil or something (to reduce evaporation and heat loss), beakers could work. As I understand it, they don't really have standard diameters for particular volumes, but that could be OK as long as people aren't afraid of parametric CAD to customize it.

Regarding my comment on metal, I was imagining the entire lid made of metal for temperature compatibility, since the entire outer vessel gets hot. I was focusing on the GL45 thread part because that is the hardest to make by hand. I realize this is getting a couple steps ahead of where things are now. I wonder if a design with clips like your Weck jars or standard taper Keck clips might be better than threads in the long run.

phaseloop, 2024-12-31:
All French presses, I've had or seen have a glass spout and technically are no different from a large beaker. We risk people chasing particular models of French presses. Another way is just using a glass jar but fitting the lid into internal hole diameter instead of using threads.

While whole metal lid would be nice - 3D printing it would be cost-prohibitive and difficult (external contracting). A middle-ground would be a heat-resistant GL45 thread (metal, resin) and the rest of the lid separated from hot elements (rubber gasket, etc). This should be an easy to add option as not all recipes call for high temperature that would damage the lid/thread.

sparklestheunicorn, 2025-01-07:
@with-eight-hands This is an amazing first crack at both the reactor hardening issue and the jar internationalization issue. Would love to get the FreeCAD files added to the parts repo as a Reactor Core variant when you think they're ready. It's OK if they're still "alpha" - we can add a README that explains the status and suggests directions for further development. Thanks for this thoughtful contribution to the project!

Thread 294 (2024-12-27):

### ISSUE TITLE
PARTS: CU-RLY 4 Channel Relay Board is listed twice in the parts list

### ISSUE THREAD

**Issue by pablo-01** [FourThievesVinegar/solderless-microlab#294]
Hi, I'm starting with control unit. Got all the printable parts ready and now ordering parts from the list. 

CU-RLY: '4 Channel Relay Board' is listed twice in the Control Unit section - do I need two of them or is this a mistake? 

Thanks.

**Comment by phaseloop** [comment]
It's most likely a mistake.

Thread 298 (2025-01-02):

FourThievesVinegar/solderless-microlab #298: Move GPIO handling from python3-libgpiod to native gpdiod v2 python package

phaseloop, 2025-01-02:
python3-libgpiod system package was abandoned at version 1.5.4 and all development moved to native python package "gpiod".
Old package also seems to not be compatible with python docker images.

The issue is gpiod v2 package API is slightly different from the previous one and throws some errors on device initialization. This needs to be debugged and fixed. Then all references to python3-libgpiod should be removed and gpiod should be added to requirements.txt

mushkevych, 2025-05-11:
perhaps something like this will work:

  * rename `backend/hardware/gpiochip/gpiod.py` to `backend/hardware/gpiochip/gpiod_chip.py` in order to avoid naming collisions for the `gpiod`

```
from hardware.gpiochip.base import GPIOChip
import gpiod
from gpiod.line import LineSettings, Direction, Value
from util.logger import MultiprocessingLogger
from typing import Dict, List, Union, Any

LINE_REQ_DIR_OUT: str = 'output'
LINE_REQ_DIR_IN: str = 'input'

class GPIODChip(GPIOChip):
    def __init__(self, gpio_config: Dict[str, Any]) -> None:
        """
        Initializes the GPIO chip configuration.

        :param gpio_config: dict with keys:
            - chipName: device path for the gpiochip (e.g., '/dev/gpiochip0')
            - lineAliases: optional dict mapping alias strings to line offsets
        """
        self._logger = MultiprocessingLogger.get_logger(__name__)
        self.chip_name: str = gpio_config['chipName']
        self.line_aliases: Dict[str, int] = gpio_config.get('lineAliases', {})
        self.output_offsets: List[int] = []
        self.output_values: List[int] = []
        self._logger.debug(f"Configured chip {self.chip_name} with aliases {self.line_aliases}")

    def _get_line_number(self, pin: Union[str, int]) -> int:
        """
        Resolve a pin alias or return the numeric offset.
        """
        if isinstance(pin, str):
            if pin in self.line_aliases:
                return self.line_aliases[pin]
            raise ValueError(f"Invalid GPIO pin alias: {pin}")
        return pin

    def _commit_output(self) -> None:
        """
        Batch-request all configured lines as outputs and set their values using the modern API,
        opening and closing the chip device each time via context manager.
        """
        if not self.output_offsets:
            return

        config: Dict[int, LineSettings] = {}
        for off, val in zip(self.output_offsets, self.output_values):
            ls = LineSettings()
            ls.direction = Direction.OUTPUT
            ls.output_value = Value.ACTIVE if val else Value.INACTIVE
            config[off] = ls

        with gpiod.Chip(self.chip_name) as chip:
            with chip.request_lines(config=config, consumer="microlab") as req:
                # Initial values set by request_lines; nothing else required
                pass

    def setup(
        self,
        pin: Union[str, int],
        pinType: str = LINE_REQ_DIR_OUT,
        outputValue: int = 0
    ) -> None:
        """
        Configure a pin for output (only output supported).

        :param pin: alias or numeric line offset
        :param pinType: 'output' or 'input'
        :param outputValue: initial value (0 or 1)
        """
        line = self._get_line_number(pin)
        if pinType != LINE_REQ_DIR_OUT:
            raise NotImplementedError("Only output pins are supported")

        if line in self.output_offsets:
            idx = self.output_offsets.index(line)
            self.output_values[idx] = outputValue
        else:
            self.output_offsets.append(line)
            self.output_values.append(outputValue)

        self._commit_output()

    def output(
        self,
        pin: Union[str, int],
        value: int
    ) -> None:
        """
        Update the output value for a configured pin.

        :param pin: alias or numeric line offset
        :param value: 0 or 1
        """
        line = self._get_line_number(pin)
        if line not in self.output_offsets:
            raise ValueError(f"Pin {pin} has not been set up for output")

        idx = self.output_offsets.index(line)
        self.output_values[idx] = value
        self._commit_output()

```

0phelia36, 2025-05-19:
Completed in #323

closed 2025-05-19 by 0phelia36

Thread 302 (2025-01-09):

FourThievesVinegar/solderless-microlab #302: As a user, I want a wide range of options for cooling the MicroLab

sparklestheunicorn, 2025-01-09:
Currently, the MicroLab can be cooled with an ice bath and a circulating fluid like water, acetone, or alcohol. We would like to have a wide range of options that can support a wide range of temperatures for long periods of time.

A collection of common cooling bath solvents and containers is here: https://chem.libretexts.org/Bookshelves/Organic_Chemistry/Organic_Chemistry_Lab_Techniques_(Nichols)/01%3A_General_Techniques/1.04%3A_Heating_and_Cooling_Methods/1.4J%3A_Cooling_Baths

We may also want to consider options that require less manual attention (restocking ice may be necessary for a DIY ice bath). A small cheap chest freezer is one potential solution: https://www.homedepot.com/pep/Magic-Chef-3-5-cu-ft-Manual-Defrost-Chest-Freezer-in-White-HMCF35W5/313922431

phaseloop, 2025-01-10:
Yeah, chest freezer or front-loaded "mini freezer" would probably be the best and cheapest solutions unless someone want to play DIY with compressors and plate heat exchangers (which won't be cheaper at all). Seems front loaded mini freezers are smaller than chest ones.

Depending on a model front-loaded mini freezers reach -22 to -14C as minimal temp.

sparklestheunicorn, 2025-10-20:
Docs have been updated to recommend some cooling solutions. Calling this closed.

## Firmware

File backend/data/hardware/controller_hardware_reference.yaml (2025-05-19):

devices:
  ## TYPE: GPIOCHIP
  ## Supported implementations:
  ## gpiod, gpiod_chipset, grbl, simulation
  - id: "gpiochip-gpiod-example"
    type: "gpiochip"
    # This implementation controls the gpio pins using libgpiod.
    implementation: "gpiod"
    # path to the chip for gpiod to use
    chipName: "/dev/gpiochip1"
    # Dictionary mapping strings to gpiod line numbers
    # Aliases taken from running gpioinfo on the device, or can be found in
    # the documentation for the board itself.
    # This example is taken from the potato (AML-S905X-CC), and you can reference
    # the documentation at the following link for some more info on what pins
    # map to what lines (the linux # column is the line #), and how that compares here.
    # https://docs.google.com/spreadsheets/d/1U3z0Gb8HUEfCIMkvqzmhMpJfzRqjPXq7mFLC-hvbKlE/edit#gid=0
    # For using another board either install libgpiod and run gpioinfo on your
    # device, or find the equivalent documentation for your board online.
    # You may end up with multiple chips, and thus need multiple devices.
    # See the AML-S905X-CC file for an example with two gpiochips
    lineAliases:
      Eth_Link_LED: 14
      Eth_Activity_LED: 15
      HDMI_HPD: 16
      HDMI_SDA: 17
      HDMI_SCL: 18
      9J1_Header_Pin2: 20
      2J3_Header_Pin6: 22
      2J3_Header_Pin5: 23
      2J3_Header_Pin4: 24
      2J3_Header_Pin3: 25
      eMMC_D0: 26
      eMMC_D1: 27
      eMMC_D2: 28
      eMMC_D3: 29
      eMMC_D4: 30
      eMMC_D5: 31
      eMMC_D6: 32
      eMMC_D7: 33
      eMMC_Clk: 34
      eMMC_CMD: 36
      ALT_BOOT_MODE: 37
      MMC_Data_Strobe: 41
      SDCard_D1: 42
      SDCard_D0: 43
      SDCard_CLK: 44
      SDCard_CMD: 45
      SDCard_D3: 46
      SDCard_D2: 47
      VCCK_Enable: 74
      7J1_Header_Pin27: 75
      7J1_Header_Pin28: 76
      VCCK_Regulator: 77
      VDDEE_Regulator: 78
      7J1_Header_Pin22: 79
      7J1_Header_Pin26: 80
      7J1_Header_Pin36: 81
      7J1_Header_Pin38: 82
      7J1_Header_Pin40: 83
      7J1_Header_Pin37: 84
      7J1_Header_Pin33: 85
      7J1_Header_Pin35: 86
      7J1_Header_Pin19: 87
      7J1_Header_Pin21: 88
      7J1_Header_Pin24: 89
      7J1_Header_Pin23: 90
      7J1_Header_Pin8: 91
      7J1_Header_Pin10: 92
      7J1_Header_Pin16: 93
      7J1_Header_Pin18: 94
      7J1_Header_Pin32: 95
      7J1_Header_Pin29: 96
      7J1_Header_Pin31: 97
      7J1_Header_Pin7: 98
      BCM_4: 98
      BCM_5: 96
      BCM_6: 97
      BCM_7: 80
      BCM_8: 89
      BCM_9: 88
      BCM_10: 87
      BCM_11: 90
      BCM_12: 95
      BCM_13: 85
      BCM_14: 91
      BCM_15: 92
      BCM_16: 81
      BCM_19: 86
      BCM_20: 82
      BCM_21: 83
      BCM_23: 93
      BCM_24: 94
      BCM_25: 79
      BCM_26: 84

  - id: "gpiochip-gpiod_chipset-example"
    type: "gpiochip"
    # This implementation combines many other gpiochip devices that use gpiod
    # into just one. lineAliases are used to determine which device to send
    # a request to. If using line numbers directly, they get sent to defaultChipID
    implementation: "gpiod_chipset"
    # device id of the default chip, this is where line requests not matching
    # any alias will be sent to
    defaultChipID: "gpiochip1"
    # Additional gpiochip device ids to use the aliases of.
    additionalChips: ["gpiochip0"]
    dependencies: ["gpiochip1", "gpiochip0"]

  - id: "gpiochip-grbl-example"
    type: "gpiochip"
    # Uses M65 and M64 commands to switch gpio pins through grbl
    implementation: "grbl"
    # id of the grbl device to send commands to
    grblID: "grbl-primary"
    # Dictionary mapping strings to grbl pin numbers
    lineAliases:
      GPIO1: 1
      GPIO2: 2
      GPIO3: 3
      GPIO4: 4
      GPIO5: 5
      GPIO6: 6

  - id: "gpiochip-simulation-example"
    type: "gpiochip"
    # This does nothing but provides dummy code to emulate the gpiod interface.
    implementation: "simulation"
    # Dictionary mapping strings to gpiod line numbers
    lineAliases:
      ID_SDA: 0
      ID_SCL: 1
      SDA1: 2
      SCL1: 3
      GPIO_GCLK: 4
      GPIO5: 5
      GPIO6: 6
      SPI_CE1_N: 7
      SPI_CE0_N: 8
      SPI_MISO: 9
      SPI_MOSI: 10
      SPI_SCLK: 11
      GPIO12: 12
      GPIO13: 13
      TXD1: 14
      RXD1: 15
      GPIO16: 16
      GPIO17: 17
      GPIO18: 18
      GPIO19: 19
      GPIO20: 20
      GPIO21: 21
      GPIO22: 22
      GPIO23: 23
      GPIO24: 24
      GPIO25: 25
      GPIO26: 26
      GPIO27: 27
      HDMI_HPD_N: 28
      STATUS_LED_G: 29
      CTS0: 30
      RTS0: 31
      TXD0: 32
      RXD0: 33
      SD1_CLK: 34
      SD1_CMD: 35
      SD1_DATA0: 36
      SD1_DATA1: 37
      SD1_DATA2: 38
      SD1_DATA3: 39
      PWM0_OUT: 40
      PWM1_OUT: 41
      ETH_CLK: 42
      WIFI_CLK: 43
      SDA0: 44
      SCL0: 45
      SMPS_SCL: 46
      SMPS_SDA: 47
      SD_CLK_R: 48
      SD_CMD_R: 49
      SD_DATA0_R: 50
      SD_DATA1_R: 51
      SD_DATA2_R: 52
      SD_DATA3_R: 53
      BCM_0: 0
      BCM_1: 1
      BCM_2: 2
      BCM_3: 3
      BCM_4: 4
      BCM_5: 5
      BCM_6: 6
      BCM_7: 7
      BCM_8: 8
      BCM_9: 9
      BCM_10: 10
      BCM_11: 11
      BCM_12: 12
      BCM_13: 13
      BCM_14: 14
      BCM_15: 15
      BCM_16: 16
      BCM_17: 17
      BCM_18: 18
      BCM_19: 19
      BCM_20: 20
      BCM_21: 21
      BCM_22: 22
      BCM_23: 23
      BCM_24: 24
      BCM_25: 25
      BCM_26: 26
      BCM_27: 27
      BCM_28: 28
      BCM_29: 29
      BCM_30: 30
      BCM_31: 31
      BCM_32: 32
      BCM_33: 33
      BCM_34: 34
      BCM_35: 35
      BCM_36: 36
      BCM_37: 37
      BCM_38: 38
      BCM_39: 39
      BCM_40: 40
      BCM_41: 41
      BCM_42: 42
      BCM_43: 43
      BCM_44: 44
      BCM_45: 45
      BCM_46: 46
      BCM_47: 47
      BCM_48: 48
      BCM_49: 49
      BCM_50: 50
      BCM_51: 51
      BCM_52: 52
      BCM_53: 53

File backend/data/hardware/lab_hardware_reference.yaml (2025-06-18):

devices:
  ## TYPE: thermometer
  ## Supported implementations:
  ## w1_therm, serial, simulation
  - id: "thermometer-w1_therm-example"
    type: "thermometer"
    # w1_therm: Supports the DS18S20, DS1822, DS18B20, DS28EA00 and DS1825/MAX31850K
    #           sensors using the 1 wire protocol. You'll need to add "dtoverlay=w1-gpio"
    #           to /boot/config.txt and reboot to use this on a pi, see https://github.com/libre-computer-project/libretech-wiring-tool
    #           for enabling the w1-gpio overlay on the AML-S905X-CC
    implementation: "w1_therm"

  - id: "thermometer-serial-example"
    type: "thermometer"
    # serial: reads the sensor data from a serial device
    implementation: "serial"
    # Which device to read data from.
    serialDevice: "/dev/ttyUSB0"

  - id: "thermometer-simulation-example"
    type: "thermometer"
    # Simulates an actual thermometer. Only reads one temperature value.
    implementation: "simulation"
    # what temperature should this thermometer always read at
    temp: 24

  ## TYPE: tempController
  ## Supported implementations:
  ## basic, simulation
  - id: "tempController-basic-example"
    type: "tempController"
    # basic: Basic hardware setup using two sets of pumps and a heating element
    #        some currently incomplete instructions for this are in docs/assembly
    implementation: "basic"
    # device ID of the thermometer to use for detecting reactor temperature
    thermometerID: "reactor-thermometer"
    # Maximum and minimum temperature in Celsius that the hardware can support
    # The microlab v0.5 makes use of 3d printed parts made of PLA, PLA can only reach
    # ~60C before it begins to mechanically fail. If you print with a different material,
    # this may be increased, search for the glass transition temperature for your material.
    # Water of course also boils at 100C, and will slowly boil off somewhat below that
    # so consider something like Propylene Glycol instead of water as a heat exchanger fluid.
    # Also keep in mind the recommended thermometer (DS18S20) only supports -55 to 125C.
    maxTemp: 50
    minTemp: -20
    # id of the gpio device that controls the pins. In most cases
    # gpio-primary will be correct.
    gpioID: "gpio-primary"
    # GPIO pin for activating the heating element
    heaterPin: BCM_26
    # GPIO pin for activating the heater pump(s)
    heaterPumpPin: BCM_20
    # GPIO pin for activating the cooler pump(s)
    coolerPin: BCM_21
    # Optional dictionary specifying PID controller parameters.
    # If not set uses a simple on/off for controlling temperature
    # based on current readings and recipe temperature tolerances.
    pidConfig:
      # PID values, required
      P: 1
      I: 0.5
      D: 5
      ### All the following parameters of pidConfig are optional ###

      # When true uses the measurement to calculate the proportional term.
      # False uses the error instead.
      # Defaults to False
      proportionalOnMeasurement: False
      # When true uses the measurement to calculate the differential term.
      # False uses the error instead.
      # Defaults to True
      differentialOnMeasurement: True
      # Min output of the PID controller
      # Defaults to -100
      minOutput: -100
      # Max output of the PID controller
      # Defaults to 100
      maxOutput: 100
      # Total length of the duty cycle for controlling the heater and cooler in seconds.
      # Defaults to 10
      dutyCycleLength: 10
    # list of device IDs that must be setup before this device
    dependencies: ["reactor-thermometer"]

  - id: "tempController-simulation-example"
    type: "tempController"
    # simulation: Simulates temperature changes due to heater and cooler activation
    implementation: "simulation"
    # Maximum and minimum temperature in Celsius that the hardware can support
    maxTemp: 50
    minTemp: -20
    # Optional. Starting temperature in Celsius, defaults to 24 if not set
    temp: 24

  ## TYPE: reagentDispenser
  ## Supported implementations:
  ## peristalticpump, syringepump, simulation
  - id: "reagentDispenser-peristalticpump-example"
    type: "reagentDispenser"
    implementation: "peristalticpump"
    # grbl device id
    grblID: "grbl-primary"
    # Configuration for the peristaltic pump motors
    peristalticPumpsConfig:
      # F: max feed rate in mm/min
      F: 175
      X:
        # scaling factor based on initial calibration
        mmPerMl: 0.5555555
      Y:
        # scaling factor based on initial calibration
        mmPerMl: 0.5555555
      Z:
        # scaling factor based on initial calibration
        mmPerMl: 0.5555555

  - id: "reagentDispenser-syringepump-example"
    type: "reagentDispenser"
    # syringepump: The open source syringe pump referenced in the assembly documentation
    #              Uses grbl and stepper motors to dispense the reagents into the microlab
    implementation: "syringepump"
    # grbl device id
    grblID: "grbl-primary"
    # Configuration for the syringe pump motors
    syringePumpsConfig:
      X:
        # Number of mm the stepper motor moves per full revolution,
        # this is the pitch of the threaded rod
        mmPerRev: 0.8
        # Number of steps per revolution of the stepper motor, reference the documentation for the motor
        stepsPerRev: 200
        # Number of mm of movement needed to dispense 1 ml of fluid,
        # this is the length of the syringe divided by its fluid capacity
        mmPerMl: 3.5
        # Maximum speed the motor should run in mm/min
        maxMmPerMin: 240
      Y:
        # These are all the same as documented above but for the Y axis
        mmPerRev: 0.8
        stepsPerRev: 200
        mmPerMl: 3.5
        maxMmPerMin: 240
      Z:
        # These are all the same as documented above but for the Z axis
        mmPerRev: 0.8
        stepsPerRev: 200
        mmPerMl: 3.5
        maxMmPerMin: 240

  - id: "reagentDispenser-simulation-example"
    type: "reagentDispenser"
    # simulation: Does nothing but sleep to simulate dispensing a reagent
    implementation: "simulation"

  ## TYPE: stirrer
  ## Supported implementations:
  ## gpio_stirrer, simulation
  - id: "stirrer-gpio_stirrer-example"
    type: "stirrer"
    # gpio_stirrer: activates the stirrer by switching a gpio pin
    implementation: "gpio_stirrer"
    # id of the gpio device that controls the pin. In most cases
    # gpio-primary will be correct.
    gpioID: "gpio-primary"
    # GPIO pin for activating the stirrer
    stirrerPin: BCM_16

  - id: "stirrer-simulation-example"
    type: "stirrer"
    # simulation: Does nothing
    implementation: "simulation"

  ## TYPE: grbl
  ## Supported implementations:
  ## serial, simulation
  - id: "grbl-serial-example"
    type: "grbl"
    # serial: opens a serial device to send commands to grbl
    implementation: "serial"
    # device path for opening a serial connection to grbl
    grblPort: "/dev/ttyACM0"

  - id: "grbl-simulation-example"
    type: "grbl"
    # simulation: Does nothing
    implementation: "simulation"

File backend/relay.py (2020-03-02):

import RPi.GPIO as GPIO

RELAY1 = 19
RELAY2 = 26
RELAY3 = 20
RELAY4 = 21

RELAY_ON = False
RELAY_OFF = True

RELAYS = [RELAY1, RELAY2, RELAY3, RELAY4]

def set_relay(r, state):
    GPIO.output(r, state)

def all_off():
    for r in RELAYS:
        set_relay(r, RELAY_OFF)

def init_relays():
    GPIO.setmode(GPIO.BCM)
    GPIO.setwarnings(False)

    for r in RELAYS:
        GPIO.setup(r, GPIO.OUT)

    all_off()

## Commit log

2020-04-18 Added current hardware specs
2020-07-20 Untested hardware integration of temp sensor and relays
2020-09-17 Got pumpA to work. Fixed relay init. Added more logging for the temp sensor which is not working correctly at the moment
2020-09-19 Fixed temperature driver and pumpB driver
2020-12-30 add assembly instructions and images. Add manifold file to repo
2021-02-22 Add microlab manifold STEP file work in progress
    [microlab-manifold.step]
2021-10-28 remove extra print statement
2022-05-08 update flask and turn off heater when stopping
2022-06-18 add syringe pump parts to the repo
2022-08-12 Update assembly.md
    fixed image paths
2022-09-10 Add parts list and link to parts repo
    [Microlab Parts List.xlsx]
2022-11-04 Update assembly.md
    Added link to reactor manifold stl, fixed some formatting.
2022-11-14 Seperated heater control to heater and heater pump
2022-11-15 Reset the currentTasks list at the start of every recipe step
2022-11-20 Added materials list recipe documentation and example to aspirin
2022-11-27 Setup syringe pumps to dispense accurate amounts
2022-11-27 Added documentation for grbl/syringe pumps
2023-01-18 Seperated user and board hardware configuration files Added config file for the AML-S905X-CC
2023-09-11 Add Z Pump to configs
2023-09-12 Initial commit for peristaltic pumps support.
2023-09-12 More peristaltic pump support
2023-09-13 peristaltic pump bug
2023-09-13 Added missing syringe pump configuration Was accidently removed in the hardware refactor
2023-09-14 Peristaltic pumps want to be in relative positioning
2023-09-14 peristaltic pump calibration
2023-10-03 updated parts list
    [Microlab Parts List.xlsx]
2023-10-03 rename and update parts list
    [Microlab Parts List.xlsx, microlab-parts-list.xlsx]
2023-10-03 more parts list tweaks
    [microlab-parts-list.xlsx]
2023-10-03 Update assembly instructions and parts list
    [microlab-parts-list.xlsx]
2023-10-04 additional documentation updates
    [microlab-parts-list.xlsx]
2023-10-04 More docs updates!
    [microlab-parts-list.xlsx]
2023-10-20 More details on reactor housing assembly
    [microlab-parts-list.xlsx]
2023-10-20 More assembly documentation updates
    [microlab-parts-list.xlsx]
2023-11-26 Updated parts list, handle thermometer read errors.
    [microlab-parts-list.xlsx]
2023-11-30 Update assembly.md - fix image file names
2023-11-30 Add labeled diagram and update assembly docs with it
2023-12-04 Update assembly.md
    Add opening paragraph and notes
2023-12-04 Update assembly-lab-control-unit.md
    Add a note about more LCU case images
2023-12-04 Update parts list with copper tubing
    [microlab-parts-list.xlsx]
2023-12-04 Update assembly-lab-control-unit.md - note about stylus.
2023-12-07 Update parts list: Remove old tubing, add notes
    [microlab-parts-list.xlsx]
2023-12-08 A few more BOM tweaks
    [microlab-parts-list.xlsx]
2023-12-08 more temperature read tweaks
2023-12-08 Docs updates and more temperature tweaks
    [microlab-parts-list.xlsx]
2023-12-09 Ignore w1_therm error when sensor can't read data yet
2023-12-11 Comment out temperature debugging code
2023-12-11 Update default settings to use peristaltic pumps and serial thermometer
2023-12-12 Update docs with more details on the TCU
    [microlab-parts-list.xlsx]
2023-12-15 Updated parts list and docs
    [microlab-parts-list.xlsx]
2023-12-19 Add "on brand" paint colors to the parts list
    [microlab-parts-list.xlsx]
2023-12-23 Limited temperature display to 2 decimal points
2023-12-24 Removed some debug print statements
2024-01-02 Update assembly-lab-control-unit.md
    Add a detail about breadboard jumpers for pins and screw terminals
2024-01-02 Add entry for breadboard jumpers
    [microlab-parts-list.xlsx]
2024-01-11 BOM: Update links to items, small text updates
    [microlab-parts-list.xlsx]
2024-01-16 Parts list parts updates
    [microlab-parts-list.xlsx]
2024-02-15 Refactor hardware device loading
2024-03-04 Converted print() calls to use pythons logging module
2024-03-10 Update assembly-temperature-control-unit.md
    Mention off-the-shelf power brick.
2024-04-27 bugfix: add gcode to advance steppers
2024-04-27 Remove the extra newline ¯\_(ツ)_/¯
2024-05-07 Update control unit assembly and add new pics
2024-05-14 Update temperature control unit instructions
2024-05-21 Update the BOM and tweak the rest of the docs.
    [microlab-parts-list.xlsx]
2024-05-28 Update assembly.md
    PR to pull request
2024-05-28 Update assembly.md
    Make BOM link to raw blob instead of empty-looking github file url
2024-05-28 Update assembly.md
    Update printed parts list
2024-05-28 Update assembly.md
    typographical errors corrected
2024-05-28 Update assembly.md
    Clarified some verbiage
2024-05-28 Update assembly-control-unit.md
    Made photo caption look more like a photo caption
2024-05-28 Update assembly-control-unit.md
    Clarified wires and cables language
2024-05-28 Update assembly-control-unit.md
    Move rPi spy cop blurb
2024-05-28 Update assembly-control-unit.md
    Remove redundant arduino parts
2024-05-28 Update assembly-control-unit.md
    Tidy up SD card instructions
2024-05-28 Update assembly-control-unit.md
    Typo
2024-05-28 Update assembly-control-unit.md
    typo correction
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2024-06-04 More docs and parts list updates
    [microlab-parts-list.xlsx]
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2024-06-12 Docs: mention 90-degree bend micro USB cables
    [microlab-parts-list.xlsx]
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2024-06-28 Partial Restructure and update of docs
    Condensed "what about info", better index, building out the Control Unit section
    [microlab-parts-list_updateCL.xlsx]
2024-07-08 Control unit overhaul, restructure of docs
    [microlab-parts-list_july.xlsx, microlab-parts-list_updateCL.xlsx]
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2024-07-16 Current state of docs
    [microlab-parts-list.xlsx, microlab-parts-list_july.xlsx]
2024-07-21 Catch certain temperature parsing errors
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2024-07-22 Last of big push
    But never fear, small clean pushes will happen in the near future
    [microlab-parts-list.xlsx]
2024-07-22 Cleanup commit
    [microlab-parts-list.xlsx]
2024-07-23 Ease off the temperature read a little. Remove one-off error handle, use sentinel value instead.
2024-07-23 Fix serial temperature reading and simplify waiting between
2024-07-26 Tweak docs, remove extraneous images, update parts list
    [microlab-parts-list.xlsx]
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2024-07-26 Parts list tweaks, addition of syringe support and coat hanger
    [microlab-parts-list.xlsx]
2024-07-31 tweak assembly and parts docs
    [microlab-parts-list.xlsx]
2024-08-01 Docs cleanup, More wire order page
    [microlab-parts-list.xlsx]
2024-08-03 Don't fail if we try to go above max speed on a pump step. Just go as fast as we can and log a message.
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2024-08-20 Add another link to parts list for peristaltic pumps
    [microlab-parts-list.xlsx]
2024-09-11 Clean up and add detail on parts list. Update corresponding docs as well.
    [microlab-parts-list.xlsx]
2024-09-11 A bit more detail in the parts list
    [microlab-parts-list.xlsx]
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2024-09-16 In thermometer/serial_simulation.py added type hints, minor variable name changes, and made an attempted fix to SerialTempSensorSimulation.getTemp as currently it will throw an exception if called wi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
2024-09-21 Fixed mistaken call of loadHardwareConfiguration from new core back to devicelist
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2024-10-01 Add note about peristaltics availability to parts list.
    [microlab-parts-list.xlsx]
2024-11-17 Update assembly-control-unit.md
    Fix some missing images and typos
2024-11-20 Update assembly-reactor-unit.md - add syringe pump link
    Added a link to the new printable syringe pump replacement for peristaltic pumps
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2024-11-25 Update index.md - fix control unit sub-component case links
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2024-12-30 Found a better general solution to the main thread logger problem
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2025-01-03 Fix docker-compose.yml device list mapping
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2025-05-18 Removed printing chipName in error message
    It isn't used in grbl or simulation and then throws a different error
2025-05-19 Change wording of error from unsupported device type
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2025-06-21 Minor updates to BOM
    [microlab-parts-list.xlsx]
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2025-09-16 Update parts list to include new reactor core
    [microlab-parts-list.xlsx]
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2025-10-02 fix: update peristaltic calibration
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2025-10-07 Update parts list and reactor assembly
    [microlab-parts-list.xlsx]
2025-10-08 docs: photos and docs update
    [microlab-parts-list.xlsx]
2025-10-10 Update screen docs and stirring gif
    [microlab-parts-list.xlsx]
2025-10-27 chore: add part files and disk image scripts to the main repo
    [control-box-lid-v.1.1.step, control-box-lid-v.1.1.stl, control-box-v.1.0.FCStd, control-box-v.1.0.step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]
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2025-11-14 Move parts list to parts-list.md
    [microlab-parts-list.xlsx]
2025-11-15 feat: Include latest GRBL in the main repo.
    [alarm_codes_en_US.csv, build_option_codes_en_US.csv, error_codes_en_US.csv, setting_codes_en_US.csv]
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2025-12-13 docs: remove old xlsx parts list
    [microlab-parts-list.xlsx]
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
